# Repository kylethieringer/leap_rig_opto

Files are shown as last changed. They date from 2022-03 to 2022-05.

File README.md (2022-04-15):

# Opto Genetic Experiments in the LEAP rigs

For code related to running experiments, see https://github.com/murthylab/leap_rigs

This repository contains a notebook and the measurements required to create stimulus files for opto experiments in the leap rigs. 

The goal of this repo is to make creating stimulus files easy and seamless, and to have a place to store the calibration data.

The document [LEAP_Rig_Opto.pdf](Leap_Rig_Opto.pdf) contains information about the setup of the opto, the measurements taken, along with a protocol to use for running experiments on the leap rigs with optogenetics.

The notebook called [create_opto_stim.ipynb](create_opto_stim.ipynb) contains a function asking what power level you would like to use for experiments. It returns the voltage required to produce that power density for each specific rig. This is calculated by finding a line of best fit from measured datapoints

You can then create a stimulus file in the notebook or you can pass this voltage output in matlab and create the actual stimulus like this:

```
% matlab stimulus creation code:
voltage = 1.23456;
fs = 10000; % daq samplerate
stimLength = 5; % seconds
daqStimLength = fs * stimLength;

stim = [ones(daqStimLength,1)*voltage; zeros(10000, 1)];
save('opto_stims/example_stim.mat', 'stim');
```

**REMEMBER:** you need to save an rig specific .mat file onto each computer in "C:\code\leap_rigs\opto_stims"

*If you have any feedback or questions please let me know!
-Kyle*

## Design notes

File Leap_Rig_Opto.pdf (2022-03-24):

# LEAP Rig Opto

## Kyle Thieringer

Contents:
Materials
Results
Setting Up Experiments
Running Experiments
Creating Experiment Scripts Creating an Opto Stim File

### Materials

All data and code available at https://github.com/kylethieringer/leap_rig_opto.git

Green LEDs:
Name: Luxeon Green (530nm) Rebel LED on a SinkPAD-II 20mm Tri-Star Base - 489 lumens @ 700mA
Wavelength Range: 520nm to 540nm
Recommended Operating Current: 700mA
Typical Forward Voltage: 8.7 Vf
Max Forward Voltage: 10.53 Vf
Red LEDs:
Name: Luxeon Red (627nm) Rebel LED on a SinkPAD-II 20mm Tri-Star Base - 138 lumens @ 350mA
Wavelength Range: 620nm to 645nm
Recommended Operating Current: 350mA
Typical Forward Voltage: 8.7 Vf
Max Forward Voltage: 10.53 Vf
Optics:
Name: Carclo 27° Frosted 20 mm Circular Beam Optic - Integrated Legs Beam Angle: 27°
Efficiency: 85%

ThorLabs T-Cube LED Driver:
Interfaces with the computer so we can control the voltages and trigger of the led lights. Mode must be set to “MOD” for this function to work. The Current Limit was set according to the specifications of the LEDs and then fine tuned to calibrate rigs to emit relatively similar power with red leds at a given voltage.

Luxeon FlexBlock LED Driver:
These LED drivers are designed to effectively boost the forward voltage of a power source inline with the leds. They are specifically made to handle LED loads that are higher than the supplied voltage of the given power source (in our case the Thorlabs T-Cube). I do not understand the physics of this, but without it, LEDs flicker at best.

LED Rings:
Manufactured out of aluminum by the physics workshop. Designed to support 6 LEDs (alternating 3 red and 3 green). (Fig. 1a)

Wiring Diagram:
Fig. 1b illustrates the circuit in one individual chamber. Due to power limits, the user can only use one led circuit at a time. If both circuits are needed simultaneously, one simple option would be to plug the red circuit into chamber 1 flexblock and the green circuit into chamber 2 flexblock. This would mean that chamber 2 would not have any opto during the experiment but would be the controller for one of the led colors in chamber 1.

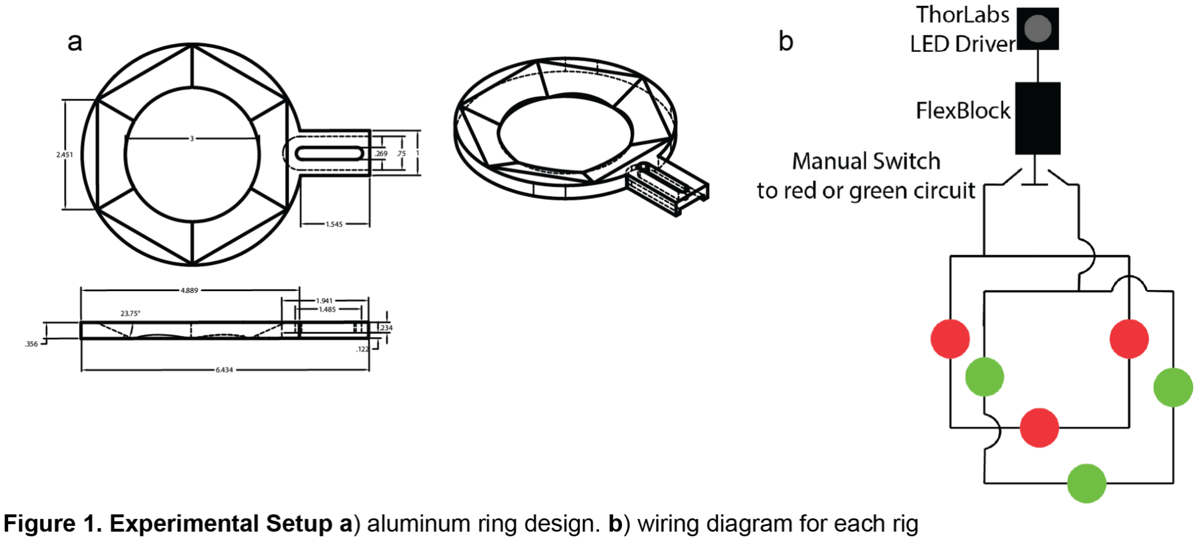
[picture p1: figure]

### Results

Power Density Readings:
The current limits of each ThorLabs T-Cube LED Driver was adjusted by measuring power from 2.5V in the red channel. This was done because the red channel is more commonly used by members in the lab. LED intensity was measured using thorlabs PM100D. The wavelength was set to 627 nm or 530 nm for red and green leds respectively.
For linearity tests, a calibration stimulus was used for each rig consisting of 10 seconds each of: 0V, .2V, .25V, .5V, .7V, 1V, 2V, 3V, 4V, 5V. The power meter sensor (Thorlabs S130VC) was placed centered on the mic array without a coverslip then light intensity values were measured for each power step. After taking measurements on two separate days, the average was taken and plotted for all rigs (Fig. 2a,b) (Tables 1,3). Despite human error in placing the sensor or other unaccounted for sources of variability, the LED intensity was very consistent

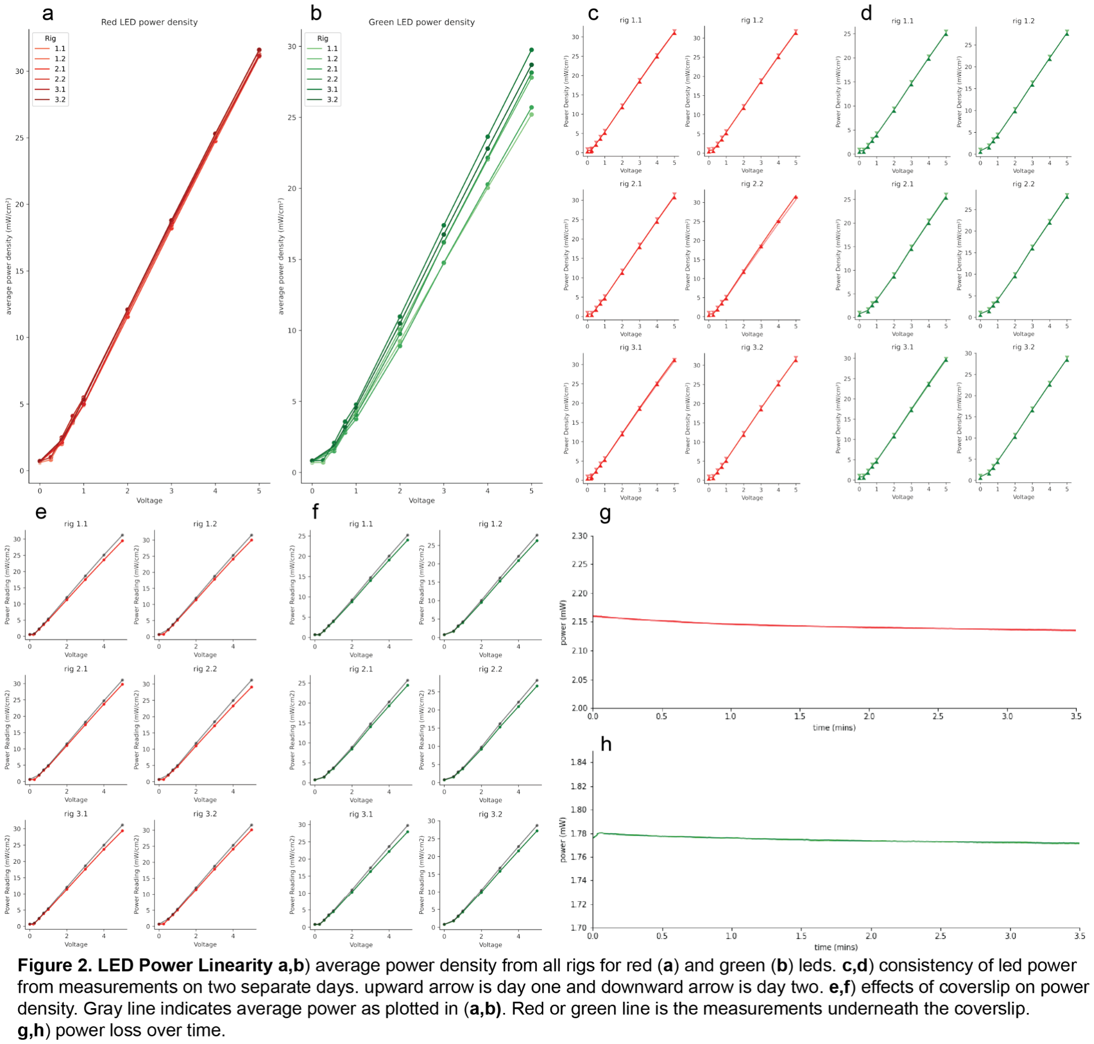
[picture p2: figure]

across days (Fig. 2c,d) (Tables 1,3). All rigs produced tightly distributed red led power densities due to calibration. While the power densities produced by green leds varied between rigs (Fig. 2b), each individual chamber was consistent across days (Fig. 2d). This allows for the user to confidently create stimuli but the voltages supplied to each chamber’s leds will vary more than what will be required in the red channel. One point to note is that there is a minimum power requirement that is slightly different between rigs. Blank values in the Tables indicate when insufficient power was supplied and thus no LED power was measured. A general rule of thumb could be to use >.25V for red LEDs (Table 1) and >.5V for green LEDs (Table 3).
To determine the effects of the coverslip on power intensity, and to account for variability from light refraction, the coverslip was placed over the power meter sensor and propped up to remain level. Again the power meter sensor was placed in the center of the chamber. The same calibration stim was used and compared to the average values found without the coverslip (Fig. 2e,f) (Tables 2,4). The coverslip reduced the measured power, but never more than 3mW/cm² for any chamber (Tables 1-4). Then the power loss over time was determined through constant power detection by the power meter over multiple minutes. The LEDs used in the setups are high powered and emit heat as well as light. Due to the nature of thermodynamics, as the LEDs heat they are becoming less efficient at producing light so it becomes crucial to draw the heat away. The LEDs are mounted on an aluminum ring for this purpose and there is minimal power loss over time (Fig2. g,h).
The homogeneity of light around the chamber was measured by placing the sensor above each of the 9 mics to remain consistent across all chambers (Fig. 3a,c). 9 measurements were taken for each chamber given 2.5V. Mics are numbered 1-9 from back to front and left to right. The difference between the max
and min values in each chamber did not
surpass 10% for the Red LEDs or 11%
for the green LEDs(Fig. 3b, d) (Tables 5,6). The variabilities in power around the chamber come from differences in individual LEDs or human error in wiring and/or mounting the LEDs. These values may further change with the addition of the coverslip, but were not measured due to the technical and laborious challenge of balancing the coverslip over the power sensor for 9 different locations in the chamber for each chamber.

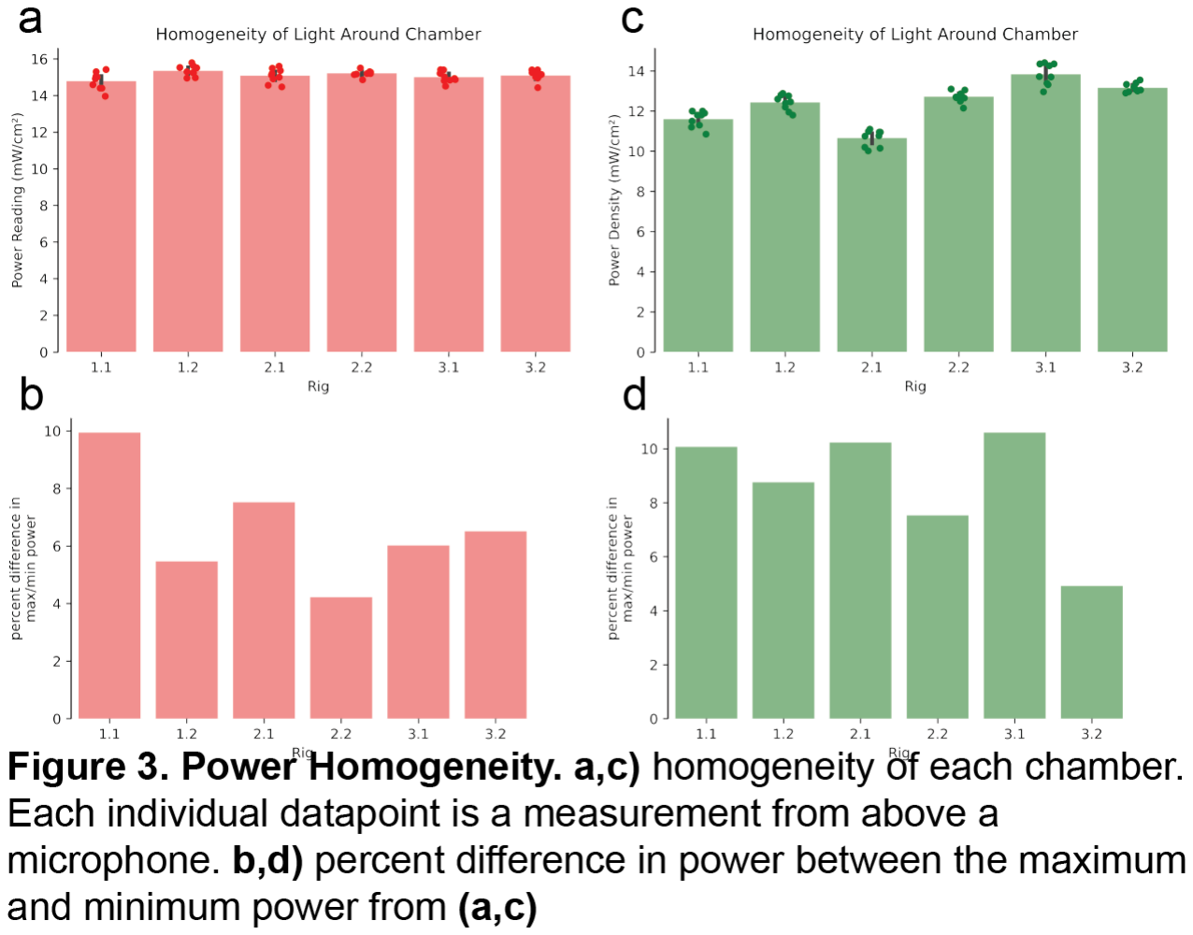
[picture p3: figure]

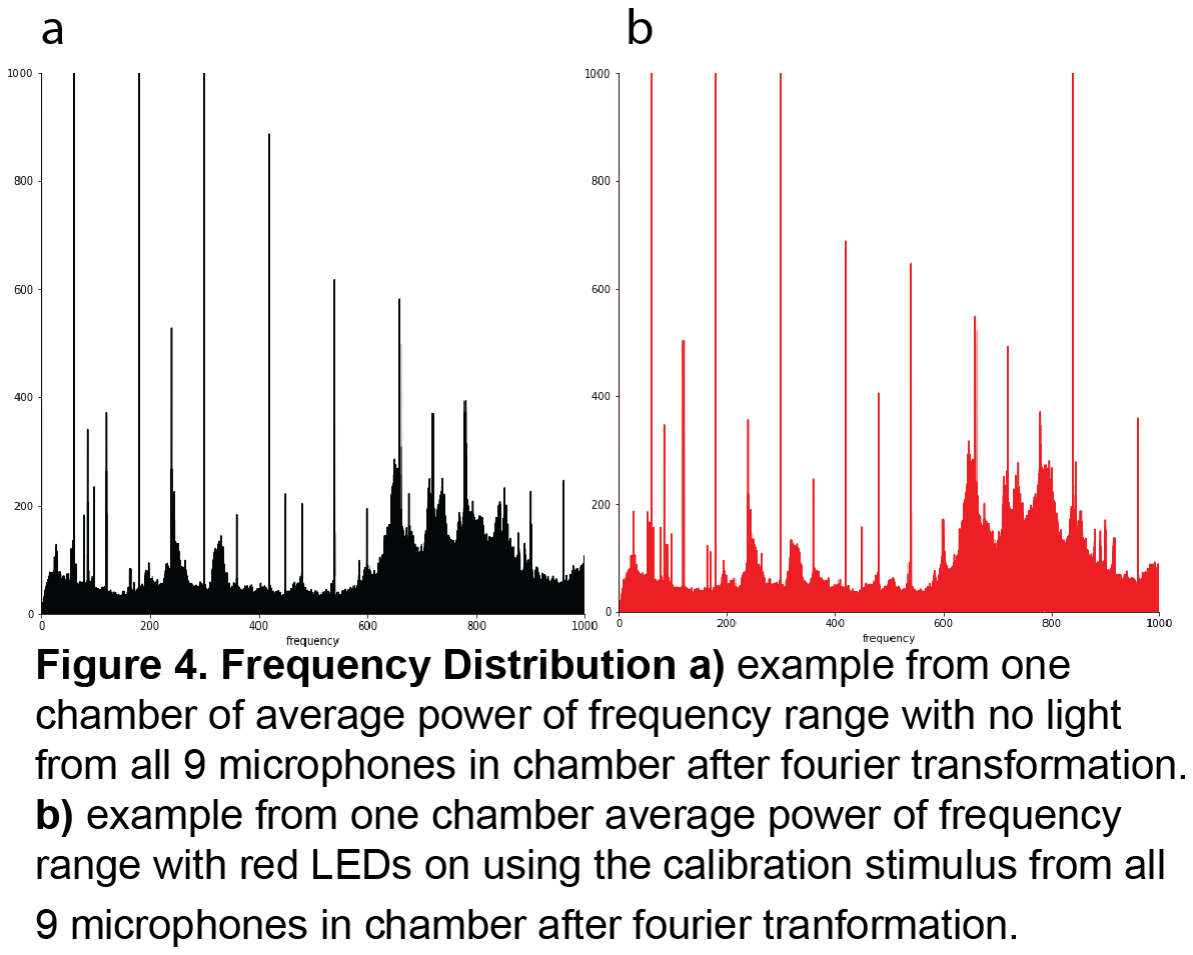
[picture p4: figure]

The microphones were checked for any sound interference that may come from the LEDs. The same calibration stimulus pattern was used, ranging from 0V to 5V for 10 seconds each. Figure 4 illustrates a representative rig with all 9 microphones transformed with a fourier transformation to visualize the amplitude of frequencies. If there was noise coming from the LEDs at any voltage, there would be a peak in the red (with lights on) but not the black (control) trace. There were no notable peaks in the range of frequencies we are mostly concerned with (0-1000hz) nor a broader range of frequencies.

### Setting Up Experiments

1. Follow all setup that you typically do in the sleap rigs to get ready for experiments, including but not limited to:
- Sigmacote coverslips
- Fill humidifiers
- Turn on IR lights
- Double check your experimental script for the correct duration, and stimulus files
2. Open Motif as you normally would and connect cameras.
- Run Baseline recordings and plot audio to check that all mics are on and working and the IR lights are on but NOT flashing
- Currently we do not have a way to view recordings live with the opto script as it stands
3. Check opto LED drivers (black Thorlabs box with knob)
- To check which LED light is plugged in, turn switch to ‘CW’ and turn the knob.
- To switch LEDs find the labeled black and red wires and switch the connection
- IMPORTANT: for opto to work with the script, the driver must be switched to ‘MOD’ and the knob must be turned to any value other than off.
4. Load flies into chambers
- Ensure that the coverslip and its holder are aligned properly. Failure to do so will leave gaps between the coverslip and the mic array. Flies are escape artists and will crawl where you don’t want them. Avoid this headache!
- I suggest loading female and male together
5. Place plastic ring on top of IR lights
- These have the simple purpose as to block the IR lights from shining up to the opto LEDs. The objectives on the optoLEDs will reflect light back onto the coverslip which will show up in the video. Using the rings also has the added benefit of increasing contrast between the black background and the illuminated flies.
- If you forget to place the ring on top of the lights you can either quit out of the experiment with ctrl-c and restart with the rings on or you can ignore it

Reminder: the opto script does not have a place to input experimental metadata such as fly genotypes, dates of birth, or manipulations. So make sure you take these notes somewhere.

### Running Experiments

1. Open cmder and type these commands: cd C:\code\leap_rigs
activate leap_rigs
- Terminal should say this: C:\code\leap_rigs (main -> origin)

(leap_rigs) λ
- Run Experiment with this:
python your_experiment_script.py
2. Experiments will be saved to “D:\Motif”
- Copy over to your personal drive somewhere
- DON’T leave files on rig computers, these are not meant for long term storage

NOTE on Canceling an Experiment: if you ctrl-c during the experiment, it will stop recording and will not save the files. However, this will not reset the daq or motif. Before running another experiment, run a short 10 second script. This will throw up an error when trying to save BUT will fully shut down everything and you will be good to go now. Better to have the error with this file than your precious data!!

### Creating your experiment script

1. Copy the file pilot_opto_v2.py from the folder “C:\code\leap_rigs” on the rig computers.
- You will need to create a new script on each computer.
2. Update your experiment parameters including:
- Experiment duration (in minutes)
- record_left_camera = True or False
- record_right_camera = True or False
- opto_stim_left = “opto_stims\example_stim_1.mat”
- opto_stim_right = “opto_stims\example_stim_2.mat”
3. Save file in C:\code\leap_rigs

NOTE: If you only want opto in the right chamber you cannot set opto_stim_left = None if record_left_camera = True. You must pass a stim of all zeros or set left camera to false

Closed Loop Opto: see this script for Talmo’s implementation of real time sleap tracking https://github.com/murthylab/leap_rigs/blob/114341d92675bae8376f3d611b94e1debf2d8c5f/leap_rigs/tracking.py (https://github.com/murthylab/leap_rigs/blob/114341d92675bae8376f3d611b94e1debf2d8c5f/leap_rigs/tracking.py)
And the DaqController class in this file for more info on how the opto stim is used by the daq controller
https://github.com/murthylab/leap_rigs/blob/114341d92675bae8376f3d611b94e1debf2d8c5f/leap_rigs/daq.py (https://github.com/murthylab/leap_rigs/blob/114341d92675bae8376f3d611b94e1debf2d8c5f/leap_rigs/daq.py)

### Creating an opto stim

Relevant code and documentation: https://github.com/kylethieringer/leap_rig_opto.git
1. The experiment script takes .mat files as input to the daq to trigger the lights. Therefore, the .mat files should be vectors of shape (samples, 1). The number of samples indicates the length of the stimulus—the daq frequency is 10,000 samples/sec, so a vector of shape (10000,1) will last one second.
2. A simple stimulus of one second on and one second off can be created with the following code in MATLAB:

stim = [ones(10000,1) * 3; zeros(10000,1)]; save(‘example_stim.mat’, ‘stim’);
3. IMPORTANT: The variable must be saved as ‘stim’ (all lowercase).
4. Voltage can be any double type
5. If the length of the stim does not equal the length of the recording, the stimulus will repeat until the end of the recording.
6. Save the stim to “C:\code\opto_stims” on each computer

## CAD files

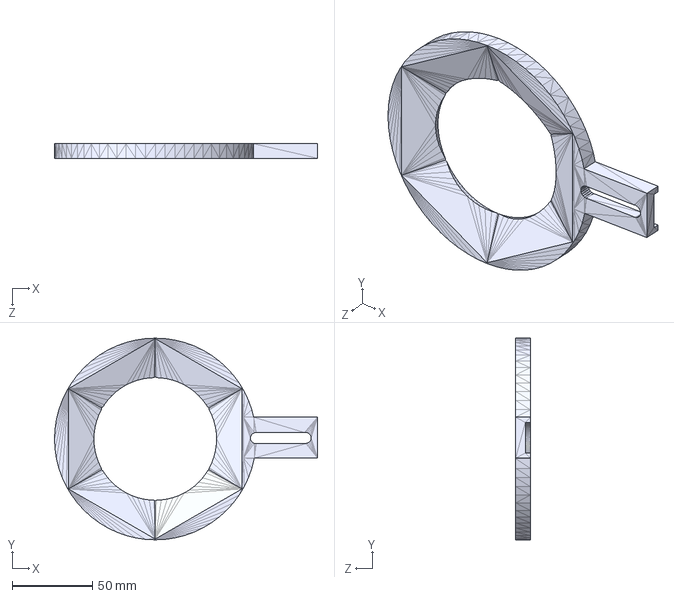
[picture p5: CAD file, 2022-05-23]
sleap led ring.STEP
163.4 x 125.3 x 9.04 mm

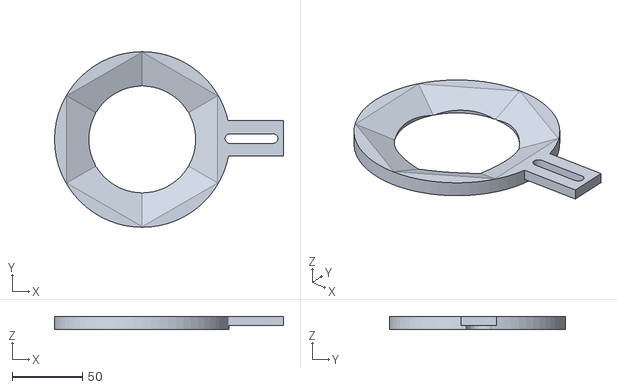
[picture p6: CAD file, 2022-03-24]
3Dprint_sleap_led_ring.stl
163.4 x 125.3 x 9.04

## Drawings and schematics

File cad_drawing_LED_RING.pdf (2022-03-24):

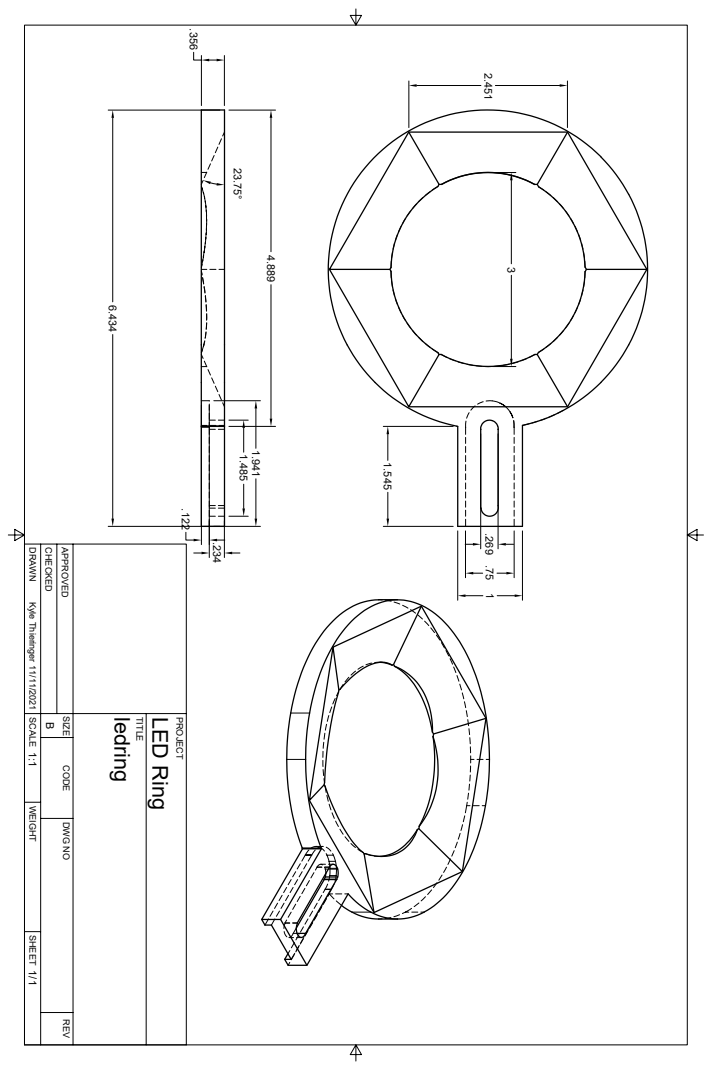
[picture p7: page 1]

TITLE PROJECT DRAWN CHECKED APPROVED SCALE WEIGHT SHEET DWG NO REV CODE SIZE 1/1 1:1 11/11/2021 Kyle Thieringer Bledring LED Ring .356 6.434 1.545 1 .269 23.75° 2.451 .234 .122 1.941 1.485 .75 3 4.889

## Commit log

2022-03-24 add led ring files
    [3Dprint_sleap_led_ring.stl]
2022-03-24 add some metadata
    [leap_rig_opto.xlsx]
2022-05-23 add step file for cnc use
    [sleap led ring.STEP]
